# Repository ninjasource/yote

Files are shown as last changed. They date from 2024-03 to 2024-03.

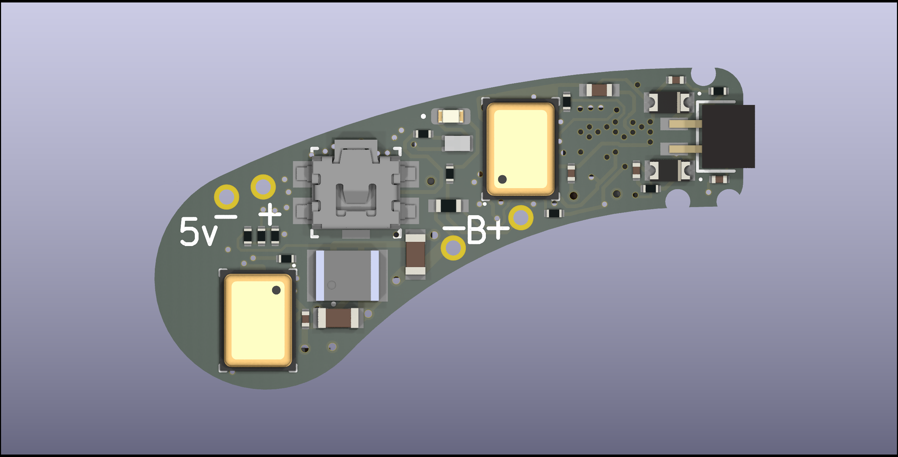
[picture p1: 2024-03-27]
kicad/yote/manufacture/yote-back.png

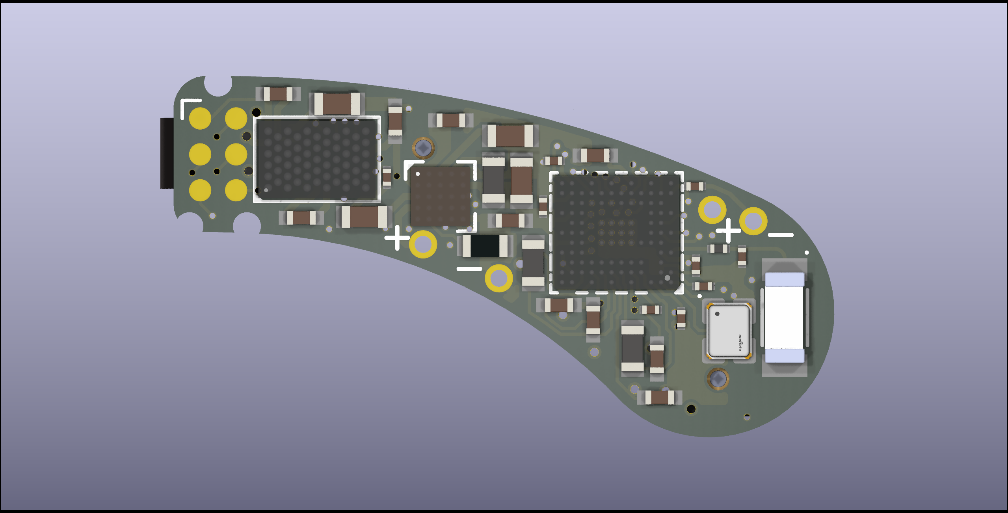
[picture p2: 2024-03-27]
kicad/yote/manufacture/yote-front.png

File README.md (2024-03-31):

# Yote - Year of the Ear

Experiments with the nrf5340 Audio Dk, CS47L63 DSP chip and Yote experimental hearing aid. 
For Rust firmware, open the `firmware` folder instead of working from this folder

## Prerequisites

`cargo install probe-rs --features="cli"`

If probe-rs does not work then a known working version can be found here:
https://github.com/probe-rs/probe-rs.git#ff2370fb

## To run

NOTE on naming:
All the examples prefixed with "yote" are for the custom built hearing aid device. Everything else is for the nRF5340 Audio-dk

IMPORTANT: be sure to set the appropriate runner in .cargo/config.toml

```
cargo run --bin blinky --release
```

## Troubleshooting

You may get an "Arm specific error at runtime and the most likely cause is that you ran probe-run with the `--erase-all` flag set.
Check the notes in `.cargo/config.toml`

Here are some commands you may find useful when working with the nrf5340 audio dk. 
You will need to install the nrfjprog command line tools from Nordic beforehand.

```
nrfjprog -i
nrfjprog --eraseall --snr 1050175639 (locks up)
nrfjprog --recover --coprocessor CP_APPLICATION --snr 1050175639
nrfjprog --recover --snr 1050175639 (same as application above)
nrfjprog --recover --coprocessor CP_NETWORK --snr 1050175639 (locks up)
```

Here is some code that you can use to flash the device without probe-run:

```
#! /usr/bin/env bash

cargo objcopy --release -- -O ihex test.hex
nrfjprog -f NRF53 --erasepage 0x00000000-0x00100000
nrfjprog -f NRF53 --program test.hex --debugreset
rm test.hex
```

## How it works

This demo uses the mcu to generate a tone and plays it into the cs47l63 dsp chip. 
Before it can do that it has to configure the dsp chip correctly by writing to various registers over spi.
There are multiple tasks running simultaneously so we need a mechanism to share the spi bus between them.

The demo runs three main tasks simultaneously: 
1. Handle interrupts from the DSP chip which indicates that long running tasks on the DSP have been completed
2. Handle button presses to control playback and volume
3. Generate a waveform in real time and push the data to the DSP chip over the I2S sound bus

## Project structure

The `cs47l63` cargo library is responsible for booting up the cs47l63 chip correctly and providing a bunch of register address and constants to be used by the application.
The `hw_dsp` (hardware digital signal processing) constrains a collection of helper functions that make calls to the `cs47l63` driver to configure it.
The `main.rs` application should use `dsp` module to exclusively communicate with the `cs47l63` even though, in theory, it could communicate directly with it through the `shared_bus` module. Right now there is some code duplication because of some power saving experiments where we need to drop the spi bus after every use. The duplicated code should be consolidated as soon as an acceptable abstraction has been designed.

## Chapro compilation

CC=arm-none-eabi-gcc
AR=arm-none-eabi-ar
CFLAGS = -W -Wall -Os -mthumb -ffunction-sections -fdata-sections -mcpu=cortex-m33 -DBR_ARMEL_CORTEXM_GCC -I$(INCDIR) -Wno-unused-local-typedef -fPIC -mfpu=fpv5-sp-d16 -mfloat-abi=hard

## Notes on Power Consumption

Here are some of the things that seem to affect power consumption:

Logging: No effect unless a debugger is attached - then huge effect
Core clock 64Mhz -> 128Mhz and Flash Cache enabled - 200uA consumption
Setting all peripheral pins to Input Low on startup - no effect, they seem to already default to their lowest power setting anyway

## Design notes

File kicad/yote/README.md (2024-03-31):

# Kicad project for schematic and PCB

Requires Kicad 8.0
Step files for the 3D rendering of the board will be checked in soon but at the moment they are not in the project path and therefore not rendered correctly. 
This messes up the PCB Design Rule checker too. Kicad projects are a little tricky to setup to work on multiple machines because of all the internal and external library files involved. 

If you do not have the correct version of Kicad installed then you can use the exported PDF schematic below:

Please see output/yote.pdf for now

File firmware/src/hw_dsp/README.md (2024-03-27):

# Hardware DSP

This module interfaces with the CS47L63 driver. The module consists of a collection of register values known to work with the nRF5340 Audio DK and Yote. It also exposes a shared bus to let different async tasks share the same SPI bus.
This shared bus design is no good for low power since it currently does not disable the SPI bus after use. Therefore there are duplicate `_spi` prefixed functions that do the same thing but without a mutex. This should be fixed soon.

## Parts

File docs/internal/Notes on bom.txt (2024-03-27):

100n
power decoupling caps: GRM033R61A104ME15D
Why? 10V Thats what was used in this video: https://www.youtube.com/watch?v=kUruN6WBgSw (see time 20:04)
Available cheaply from JLCPCB

1u
power decoupling caps: GRM033R60J105KEA2D
Why? 6.3V Available as 0201 (can't find 0402)
Available cheaply from JLCPCB

# command for generating bom:
/usr/bin/python3 "/usr/share/kicad/plugins/bom_csv_grouped_extra.py" "%I" "%O.csv" "PACKAGE" "MANUFACTURER" "Mfg Part #" "Notes"

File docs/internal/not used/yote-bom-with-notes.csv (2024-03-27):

Ref | Qnty | Value | Cmp name | Footprint | Description | Vendor | Mrf Part # | Jlcpcb part # | Notes
C1, C2, C3, C4, C5, C15, C19, C20, C21, C24, C26, C27 | 12 | 100n | C_Small | nrf5340:C_0201_0603Metric_Square | Capacitor, X5R, ±10% | Murata Electronics | GRM033R61A104ME15D | C408130
C7, C8, C9, C13, C14, C16, C22, C23, C25 | 9 | 1u | C_Small | nrf5340:C_0402_1005Metric_Square | Capacitor, X5R, ±10%, 6.3V | Murata Electronics | GRM155R60J105KE19D | C76929
C10 | 1 | 2n2 | C_Small | nrf5340:C_0201_0603Metric_Square | Capacitor, X7R, ±10%, 10V | Murata Electronics | GRM033R71A222KA01D | C161479
C11 | 2 | 0p7 | C_Small | nrf5340:C_0201_0603Metric_Square | Capacitor, Ceramic, NP0, ±0.1pF, 25V | Murata Electronics | GJM0335C1ER70BB01D | C161293 | Can’t find on jlcpcb, use global sourcing
C28, C30 | 1 | 2u2 | C_Small | nrf5340:C_0402_1005Metric_Square | Capacitor, Ceramic, X5R, ±10%, 10V | Murata Electronics | GRM155R61A225KE95D | C76993
C29, C31, C32, C33, C35 | 5 | 10u | C_Small | nrf5340:C_0603_1608Metric_Square | Capacitor, Ceramic, X5R, ±20%, 10V | Murata Electronics | GRM188R61A106KE69D | C77044
C34 | 1 | 22u | C_Small | nrf5340:C_0603_1608Metric_Square | Capacitor, X5R, ±20%, 6.3V | Murata Electronics | GRM188R61A226ME15D | C84419
D1, D2, D4 | 3 | PESD5V0V1BDSF | PESD5V0V1BDSF | nrf5340:D_0603_1608Metric_Square | Very low capacitance bidirectional ESD protection diode | Nexperia | PESD5V0V1BDSF,315 | C513113
D3 | 1 | RED_LED | LED | LED_SMD:LED_0402_1005Metric | Light emitting diode | Foshan NationStar Optoelectronics | NCD0402R1 | C130719
E1 | 1 | 2450AT18B100E | 2450AT18B100E | nrf5340:2450AT18B100E | 2.45 GHz chip antenna | Johanson Technology | 2450AT18B100E | C2917717
J2 | 1 | BC075-02-A-L-A | BC075-02-A-L-A | nrf5340:BC075-02-A-L-A | 2POS 1.0MM PITCH SOCKET, SIL, SM | GCT | BC075-02-A-L-A |  | Part no longer manufactured (by jlcpcb) but available on digikey
L1, L4 | 2 | 10u | L_Small | nrf5340:L_0603_1608Metric_MLZ1608M100WTD25 | Inductor, 250mA, ±20%, 1.05ohm. -55°C ~ 125°C | TDK | MLZ1608M100WTD25 | C2047264
L2, L3 | 2 | 2n2 | L_Small | nrf5340:L_0201_0603Metric_Square | Inductor, 600mA, ±0.1ｎH, 120mOhm | Murata Electronics | LQP03HQ2N2B02D | C1329438
L5 | 1 | 4n7 | L_Small | nrf5340:L_0201_0603Metric_Square | Inductor, 350mA, ±3% | Murata Electronics | LQP03TN4N7H02D | C86126 | As per dk bom
L6 | 1 | 2u2 | L_Small | nrf5340:L_0603_1608Metric_MLZ1608M100WTD25 | 750mA 2.2uH ±20% 390mΩ 0603 Inductors | TDK | MLP1608H2R2BT0S1 | C129931 | This is a 750mA rated part but on the dk it is a 2.5A rated part
R1, R2 | 2 | 100 | R_Small | nrf5340:R_0201_0603Metric_Square | Resistor, ±1%, 0.05W | YAGEO | RC0201FR-07100RL | C77623 | For stability of data line of mics
R3, R4 | 2 | 22 | R_Small | nrf5340:R_0201_0603Metric_Square | Resistor, ±1%, 0.05W | YAGEO | RC0201FR-0722RL | C155743 | For stability on headphone line
R5 | 1 | 100k | R_Small | nrf5340:R_0201_0603Metric_Square | Resistor, small symbol | YAGEO | RC0201FR-07100KL | C106224
R6 | 1 | 33k | R_Small | nrf5340:R_0603_1608Metric_Square | Resistor, small symbol | UNI-ROYAL | 0603WAF3302T5E | C4216 | Large so that it can be de-soldered (controls charging current) Basic part
R7, R8, R9 | 3 | 1M | R_Small | nrf5340:R_0201_0603Metric_Square | Resistor, small symbol | YAGEO | RC0201FR-071ML | C295786 | Voltage divider for batt measurement
R10 | 1 | 33 | R_Small | nrf5340:R_0402_1005Metric_Square | Resistor, small symbol | YAGEO | RC0402FR-0733RL | C138002 | For the red led
S1 | 1 | Volume Up | PTS840_GM_SMTR_LFS | nrf5340:SW_PTS840GMSMTRLFS | Push button switch | C&K | PTS840GMSMTRLFS | C221909
TH1 | 1 | Thermistor_NTC | Thermistor_NTC | nrf5340:R_0402_1005Metric_Square | 10kΩ 0.1mA ±1% 3380K ±1% 0402 NTC Thermistor | Murata Electronics | NCU15XH103F6SRC | C333993 | If no thermister then 10k resistor is fine
U1 | 1 | NRF5340-CLAA-R | NRF5340-CLAA-R | nrf5340:NRF5340-CLAA-R |  | Nordic Semiconductor | NRF5340-CLAA-R | C3606597
U2, U3 | 2 | IM69D130_PDM | IM69D130_PDM | nrf5340:MIC_IM69D130V01XTSA1_PadFix |  | Infineon Technologies | IM69D130V01XTSA1 |  | Not the same as the one on the Audio Dk. Says its no longer manufactured on jlcpcb. Available on digikey
U4 | 1 | CS47L63-CWZR | CS47L63-CWZR | nrf5340:CS47L63-CWZR |  | Cirrus Logic | CS47L63-CWZR | C3588069
U5 | 1 | NPM1100-CAAA-R7 | NPM1100-CAAA-R7 | nrf5340:NPM1100-CAAA-R7 |  | Nordic Semiconductor | nPM1100-CAAA-R7 | C3682614 | The NPM1100-CAAA-E-R7 variant on digikey is $2 (vs $10 for the the R7)
U6 | 1 | XCL210C12 | XCL210C12 | nrf5340:XCL210C12 |  | Torex Semiconductor | XCL210C121GR-G |  | Only available on Mouser
Y1 | 1 | 32Mhz 8pF | Crystal_GND24_Small | nrf5340:MP06003_Crystal | Four pin crystal, GND on pins 2 and 4, small symbol | Kyocera | CX2016DB32000D0WZRC1 | C1985237 | As per dk bom

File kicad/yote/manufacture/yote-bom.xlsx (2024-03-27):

 |  |  | YOTE – Bill of Materials
Item # | *Designator | *Qty | Manufacturer | *Mfg Part # | Description / Value | *Package/Footprint | Type | Your Instructions / Notes
1 | C1, C2, C3, C4, C5, C15, C19, C20, C21, C24, C26, C27 | 12 | Murata Electronics | GRM033R61A104KE15D | 100n | 0201 |  | Capacitor, X5R, ±10%
2 | C7, C8, C9, C13, C14, C16, C22, C23, C25 | 9 | Murata Electronics | GRM155R60J105KE19D | 1u | 0402 |  | Capacitor, X5R, ±10%, 6.3V
3 | C10 | 1 | Murata Electronics | GRM033R71A222KA01D | 2n2 | 0201 |  | Capacitor, X7R, ±10%, 10V
4 | C11 | 1 | Murata Electronics | GRM0335C1HR70WA01D | 0p7 | 0201 |  | Capacitor, NP0, ±0.1pF
5 | C28, C30 | 2 | Murata Electronics | GRM155R61A225KE95D | 2u2 | 0402 |  | Capacitor, X5R, ±20%
6 | C29, C31, C32, C33, C35 | 5 | Murata Electronics | GRM188R61A106KE69D | 10u | 0603 |  | Capacitor, Ceramic, X5R, ±20%, 10V
7 | C34 | 1 | Murata Electronics | GRM188R61A226ME15D | 22u | 0603 |  | Capacitor, X5R, ±20%, 6.3V
8 | D1, D2 | 2 | Nexperia | PESD5V0V1BDSF,315 | PESD5V0V1BDSF | 0603 |  | Very low capacitance bidirectional ESD protection diode
9 | D3 | 1 | Everlight Elec | 16-213SYGC/S530-E3/TR8 | GREEN_LED | 0402 |  | Green LED 2V forward voltage 25mA max
10 | E1 | 1 | Johanson Technology | 2450AT18B100E | ANT | SMD |  | 2.45 GHz chip antenna
11 | H3 | 1 |  |  | 5V | DNS |  | Footprint only – Do not place
12 | H4 | 1 |  |  | GND | DNS |  | Footprint only – Do not place
13 | H5 | 1 |  |  | BATT+ | DNS |  | Footprint only – Do not place
14 | H6 | 1 |  |  | BATT- | DNS |  | Footprint only – Do not place
15 | J1 | 1 |  |  | TC2030-NL | DNS |  | Footprint only – Do not place
16 | J2 | 1 | GCT | BC075-02-A-L-A | 2POS_FEMALE_1mm | SMD |  | 2POS 1.0MM PITCH SOCKET, SIL, SM
17 | L1, L4 | 2 | TDK | MLZ1608M100WTD25 | 10u | 0603 |  | Inductor, 250mA, ±20%, 1.05ohm. -55°C ~ 125°C
18 | L2 | 1 | Murata Electronics | LQP03HQ2N2B02 | 2n2 | 0201 |  | Inductor, 600mA, ±0.1ｎH, 120mOhm
19 | L6 | 1 | TDK | MLP1608H2R2BT0S1 | 2u2 | 0603 |  | 750mA 2.2uH ±20% 390mΩ 0603 Inductors
20 | Q1 | 1 | Tech Public | TP5001P3 | NPN_TRANSISTOR | SMD |  | NPN Transistor of with Hfe of around 100 for LED
21 | R1, R2 | 2 | YAGEO | RC0201FR-07100RL | 100 | 0201 |  | Resistor
22 | R3, R4 | 2 | YAGEO | RC0201FR-0722RL | 22 | 0201 |  | Resistor
23 | R5 | 1 | YAGEO | RC0201FR-07100KL | 100k | 0201 |  | Resistor
24 | R6 | 1 | UNI-ROYAL | 0603WAF3302T5E | 33k | 0603 |  | Resistor
25 | R7, R8, R9 | 3 | YAGEO | RC0201FR-071ML | 1M | 0201 |  | Resistor
26 | R10 | 1 | YAGEO | RC0201FR-071KL | 1k | 0201 |  | Resistor
27 | R11 | 1 | YAGEO | RC0201FR-07330RL | 330 | 0201 |  | Resistor
28 | S1 | 1 | C&K | PTS840GMSMTRLFS | PUSH_BTN | SMD |  | Push button sideways switch
29 | TH1 | 1 | Murata Electronics | NCU15XH103F6SRC | Thermistor_NTC | 0402 |  | 10k 0.1mA ±1% 3380K ±1% 0402 NTC Thermistor
30 | U1 | 1 | Nordic Semiconductor | NRF5340-CLAA | NRF5340-CLAA-R | SMD |  | nRF5340 microcontroller
31 | U2, U3 | 2 | Infineon Technologies | IM69D130V01XTSA1 | IM69D130_PDM | SMD |  | IM69D130 PDM microphone
32 | U4 | 1 | Cirrus Logic | CS47L63-CWZR | CS47L63-CWZR | SMD |  | CS47L63 digital signal processing IC
33 | U5 | 1 | Nordic Semiconductor | NPM1100-CAAA | NPM1100-CAAA-R7 | SMD |  | nPM1100 battery charger
34 | U6 | 1 | Torex Semiconductor | XCL210C121GR-G | XCL210C12 | SMD |  | 1_2V dcdc converter
35 | Y1 | 1 | Kyocera | CX2016DB32000D0WZRC1 | 32Mhz 8pF | CX2016 |  | Four pin crystal, GND on pins 2 and 4, small symbol, 32mhs 8pF

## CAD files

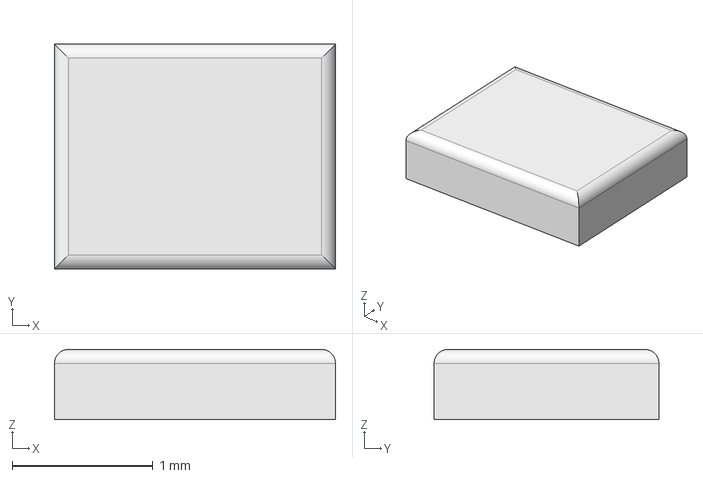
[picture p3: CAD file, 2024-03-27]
freecad/crystal/R2016-32Mhz-8pF-Crystal-Fillet.step
2.00 x 1.60 x 0.5 mm

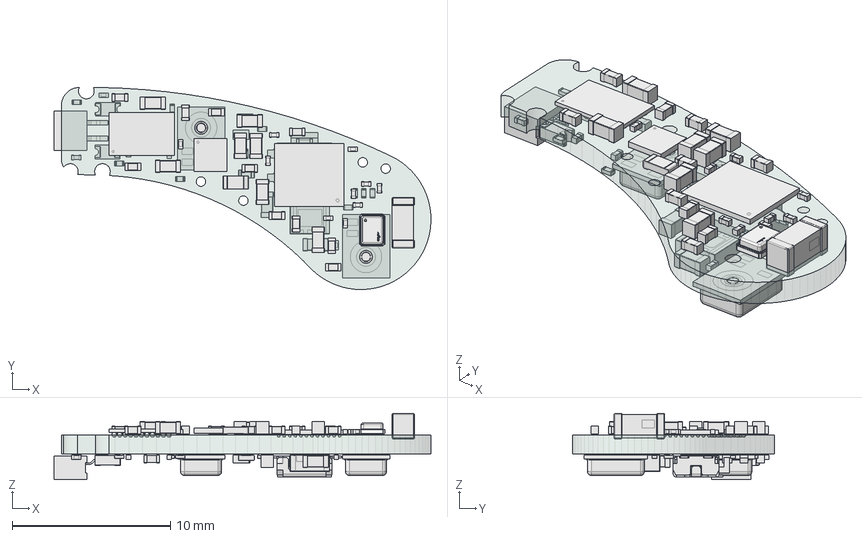
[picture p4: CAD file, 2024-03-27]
freecad/full/board.FCStd
23.8 x 12.8 x 4.17 mm
C_0402_1005Metric
L_0603_1608Metric
C_0402_1005Metric002
logo
dot
pins
C_0603_1608Metric
C_0201_0603Metric
C_0603_1608Metric002
L_0201_0603Metric
C_0201_0603Metric002
C_0402_1005Metric004
C_0201_0603Metric004
NPM1100-CAAA-R7
2450AT18B100E
C_0201_0603Metric006
C_0402_1005Metric006
C_0201_0603Metric008
C_0402_1005Metric008
C_0402_1005Metric010
C_0402_1005Metric012
C_0201_0603Metric010
C_0603_1608Metric004
C_0201_0603Metric012
C_0603_1608Metric006
R_0603_1608Metric
C_0402_1005Metric014
L_0603_1608Metric002
C_0402_1005Metric016
C_0201_0603Metric014
C_0402_1005Metric018
C_0201_0603Metric016
L_0603_1608Metric004
R_0201_0603Metric
C_0201_0603Metric018
C_0402_1005Metric020
R_0201_0603Metric002
R_0201_0603Metric004
C_0201_0603Metric020
D_0603
R_0201_0603Metric006
Y97M01840FP_G
R_0201_0603Metric008
C_0603_1608Metric008
C_0201_0603Metric022
IM69D130V01XTSA1
IM69D130V01XTSA003
XCL220B153FR-G
C_0201_0603Metric024
R_0201_0603Metric010
BC075-02-A-L-A
LED_0402_1005Metric
C_0201_0603Metric026
R_0201_0603Metric012
D_0604
R_0201_0603Metric014
R_0201_0603Metric016
R_0201_0603Metric018
C_0603_1608Metric010
R_0402_1005Metric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

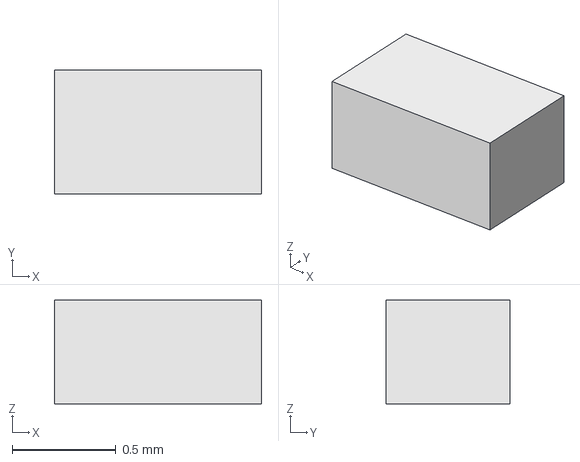
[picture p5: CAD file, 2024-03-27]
freecad/npn transistor/npn.FCStd
1.00 x 0.6 x 0.5 mm

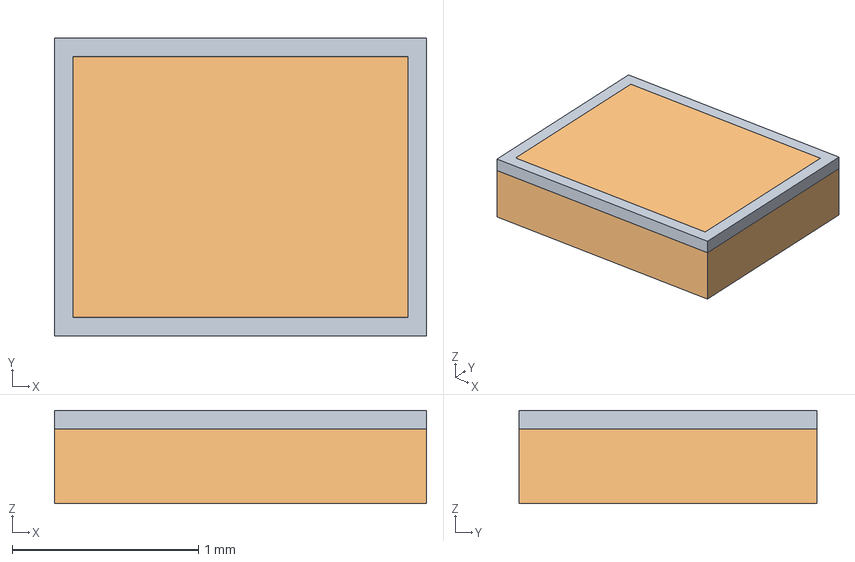
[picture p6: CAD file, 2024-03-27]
freecad/crystal/R2016-32Mhz-8pF-Crystal.FCStd
2.00 x 1.60 x 0.5 mm

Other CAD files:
freecad/npn transistor/TP5001P3.step

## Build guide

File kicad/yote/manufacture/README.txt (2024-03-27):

All vias (0.5/0.3mm and 0.3/0.15mm) to be filled and capped (because 0.3/0.15mm via-in-pad used for 0.4mm pitch bga components).
Panelization: PCWWay to please panlize board to 2 x 3 and increase the panel size accordingly.
Silkscreen: It is acceptable to not show Silkscreen on non-printable areas.
Please confirm rotation of components in a visual way with me to make sure it is correct (silkscreen should provide markers and CGI render can be used too).
Min track / spacing: 3mil
Min hole size: 0.15mm

Impedance control:

The track that connects the MCU to the antenna needs to be impedance matched to 50 ohms. Here are the calculations:

Used this calculator for surface microstrip for antenna line:
https://www.pcbway.com/pcb_prototype/impedance_calculator.html

w      = 0.134mm (calculated track width)
t Cu   = 35um (track height - I included the plating - should I have?)
h      = 0.08mm (isolation height)
Er     = 4.29 (Dialectric constant - FR4 - Standard 4.3)
Z0     = 50.0 ohm (Impedance)
Layer  = L1 (Front - yote-F_Cu.gbr)
Type   = Single ended
Pos    = x 19.45 y 6.85 (the short transmission line that L2 sits on going from the nrf5340 mcu to the antenna)
Tollerance = 10%

Used this stackup tool:
https://www.pcbway.com/multi-layer-laminated-structure.html?tdsourcetag=s_pcqq_aiomsg

Board Stackup:

Use PCBWay defaults for 8 layer board 1mm thickness
Number of Layers:   8
Board Thickness:    1 mm
Copper thickness:   1 oz

Stackup:

L1	 	Copper 18 um--plating to 35um
 	 	 
 	 	PP 0.08 mm(1080) dielectric constant 4.29 ± (The DK value is not absolute and will vary depending on the base material's models and thickness.)
 	 	 
L2	 	 
 	 	Core 0.2mm with 1/1 oz Cu
L3	 	 
 	 	 
 	 	PP 0.08 mm(1080) dielectric constant 4.29 ± (The DK value is not absolute and will vary depending on the base material's models and thickness.)
 	 	 
L4	 	 
 	 	Core 0.2mm with 1/1 oz Cu
L5	 	 
 	 	 
 	 	PP 0.08 mm(1080) dielectric constant 4.29 ± (The DK value is not absolute and will vary depending on the base material's models and thickness.)
 	 	 
L6	 	 
 	 	Core 0.2mm with 1/1 oz Cu
L7	 	 
 	 	 
 	 	PP 0.08 mm(1080) dielectric constant 4.29 ± (The DK value is not absolute and will vary depending on the base material's models and thickness.)
 	 	 
L8	 	Copper 18 um--plating to 35um

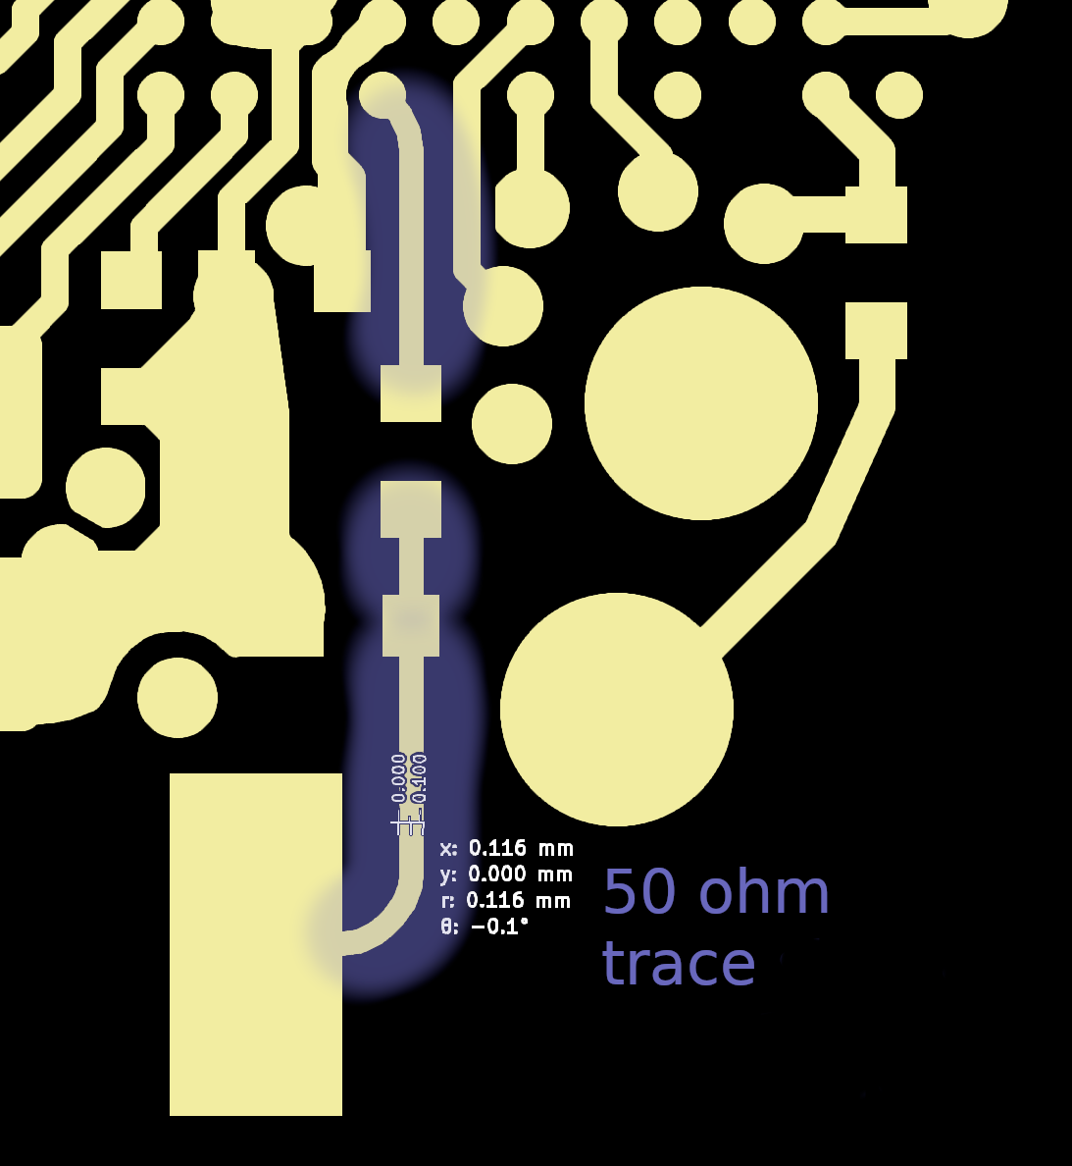
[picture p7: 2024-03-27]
kicad/yote/manufacture/gtl-impedance trace.png

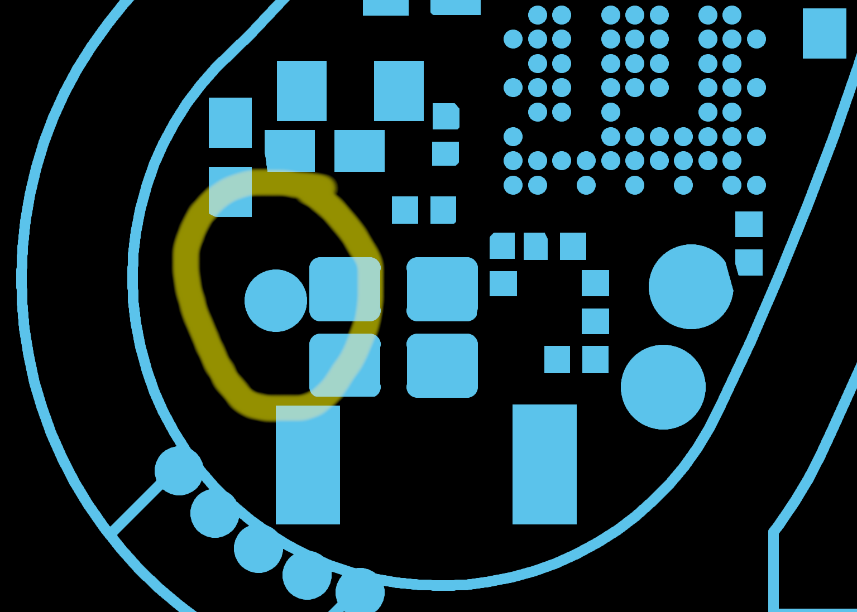
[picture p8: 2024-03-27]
kicad/yote/manufacture/gts-mic hole proximity.png

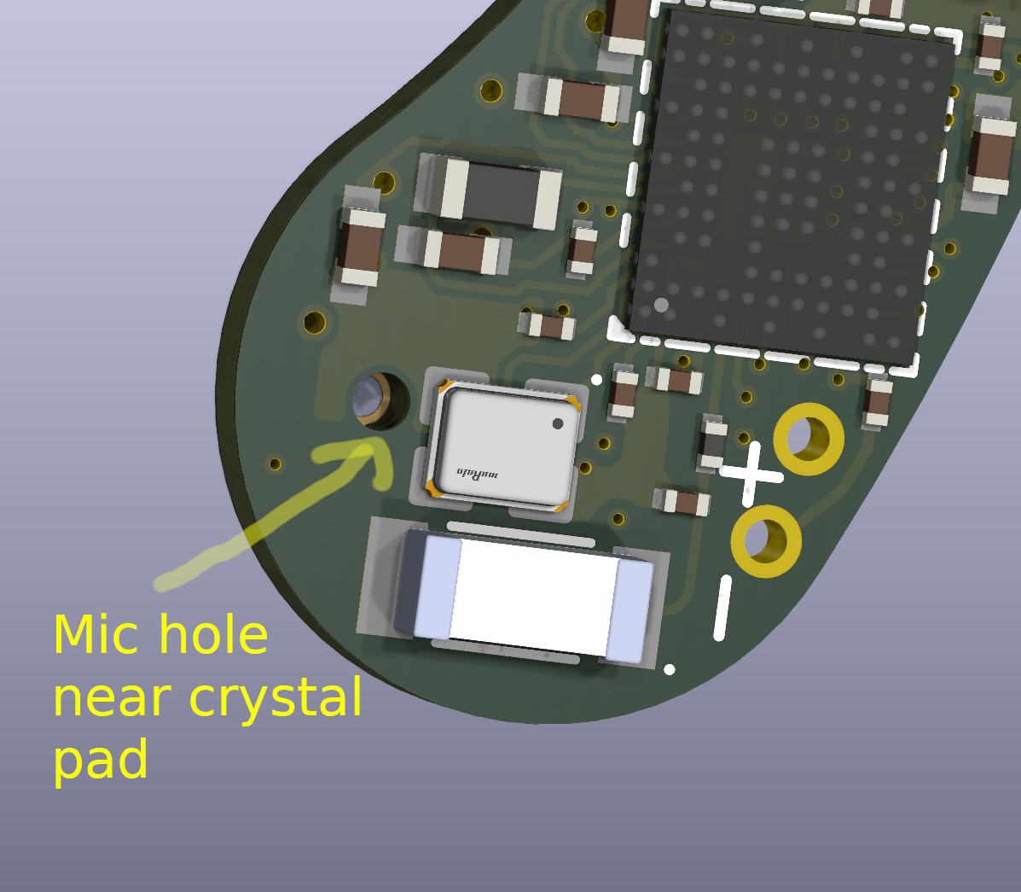
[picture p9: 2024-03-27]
kicad/yote/manufacture/gts-mic hole render.png

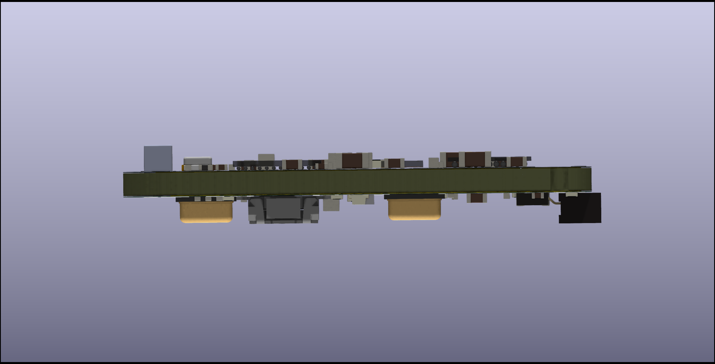
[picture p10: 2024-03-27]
kicad/yote/manufacture/yote-side.png

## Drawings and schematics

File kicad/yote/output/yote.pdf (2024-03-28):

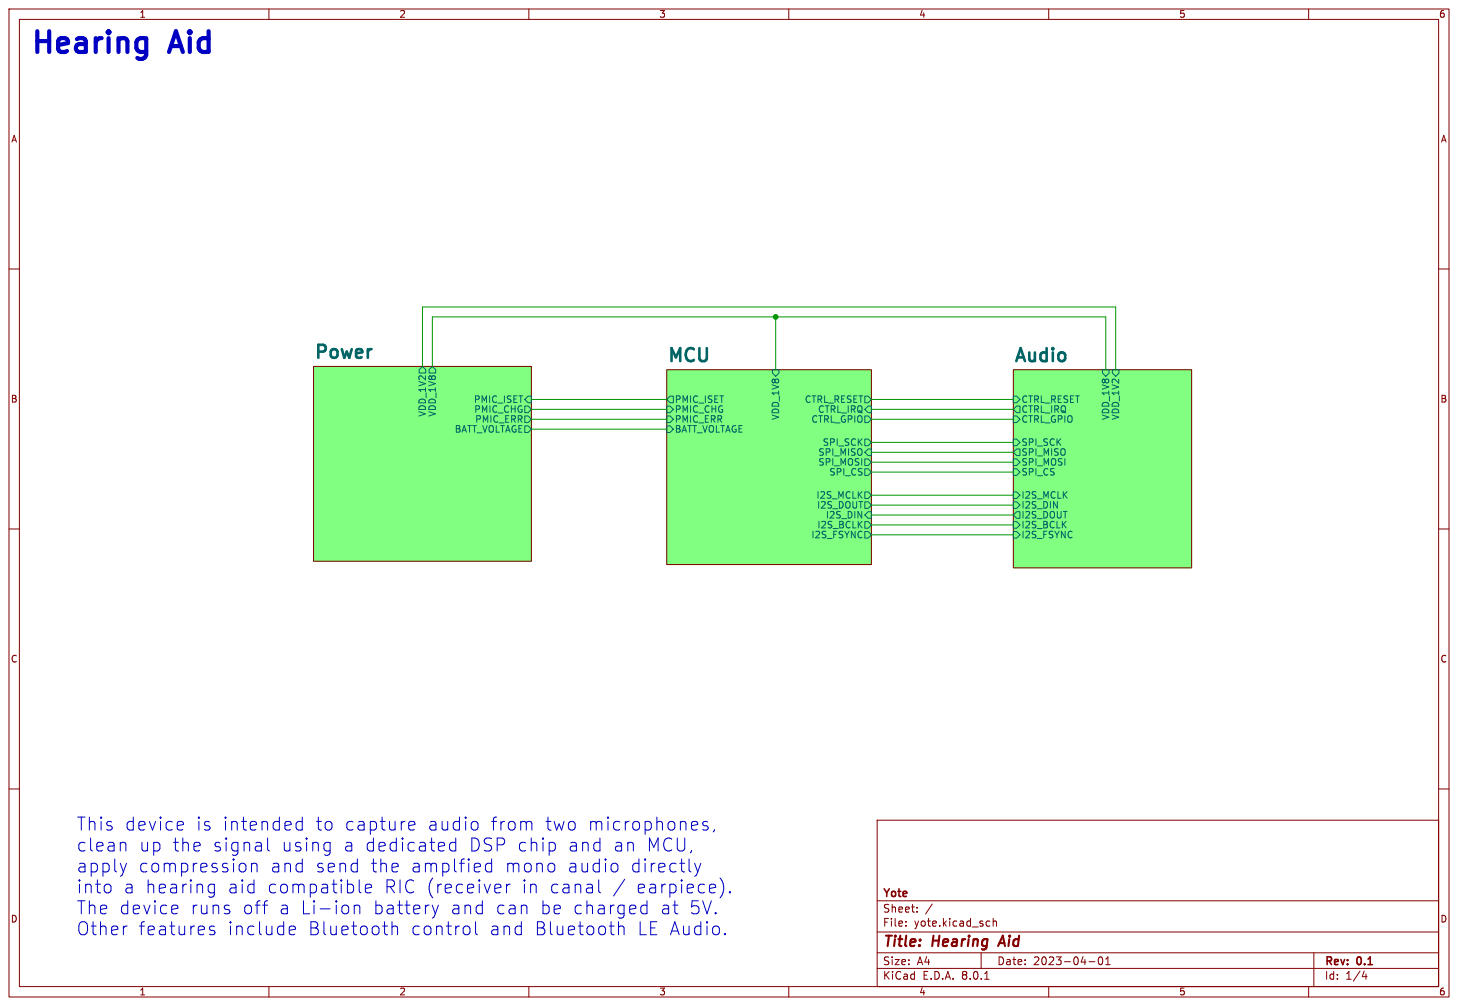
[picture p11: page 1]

File: yote.kicad_sch Sheet: / Yote

Id: 1/4 Title: Hearing Aid

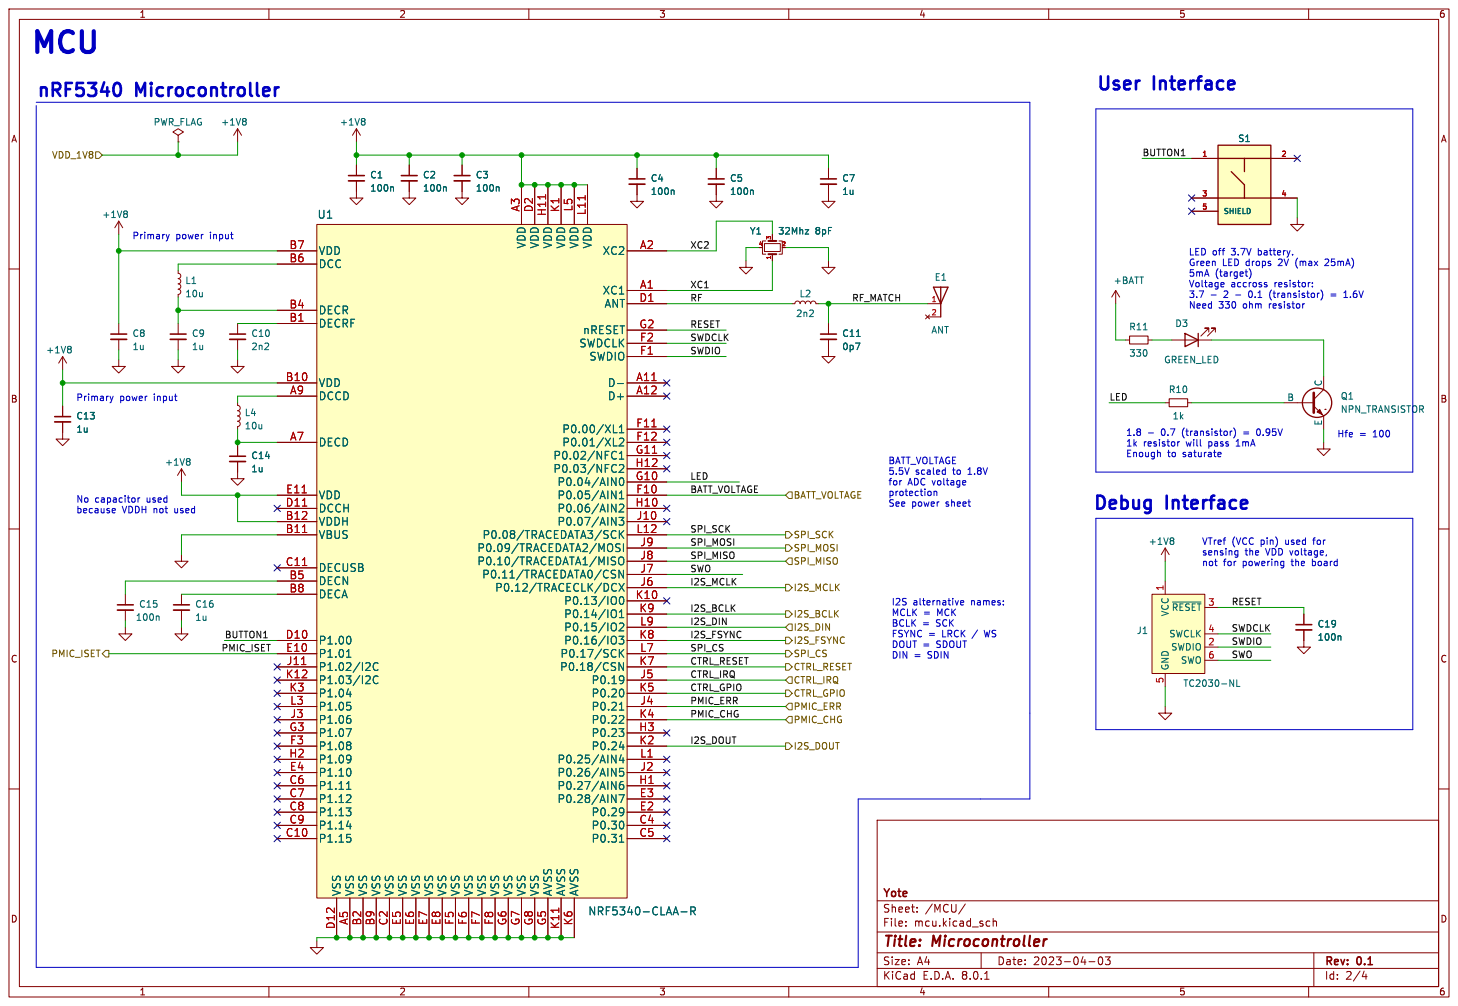
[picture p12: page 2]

because VDDH not used MCU

LED off 3.7V battery. Green LED drops 2V (max 25mA) 5mA (target)

1 SWDIO 2 ~{RESET}3 SWCLK 4 GND

Id: 2/4 Title: Microcontroller File: mcu.kicad_sch Sheet: /MCU/ Yote C16

BCLK = SCK
FSYNC = LRCK / WS DOUT = SDOUT DIN = SDIN

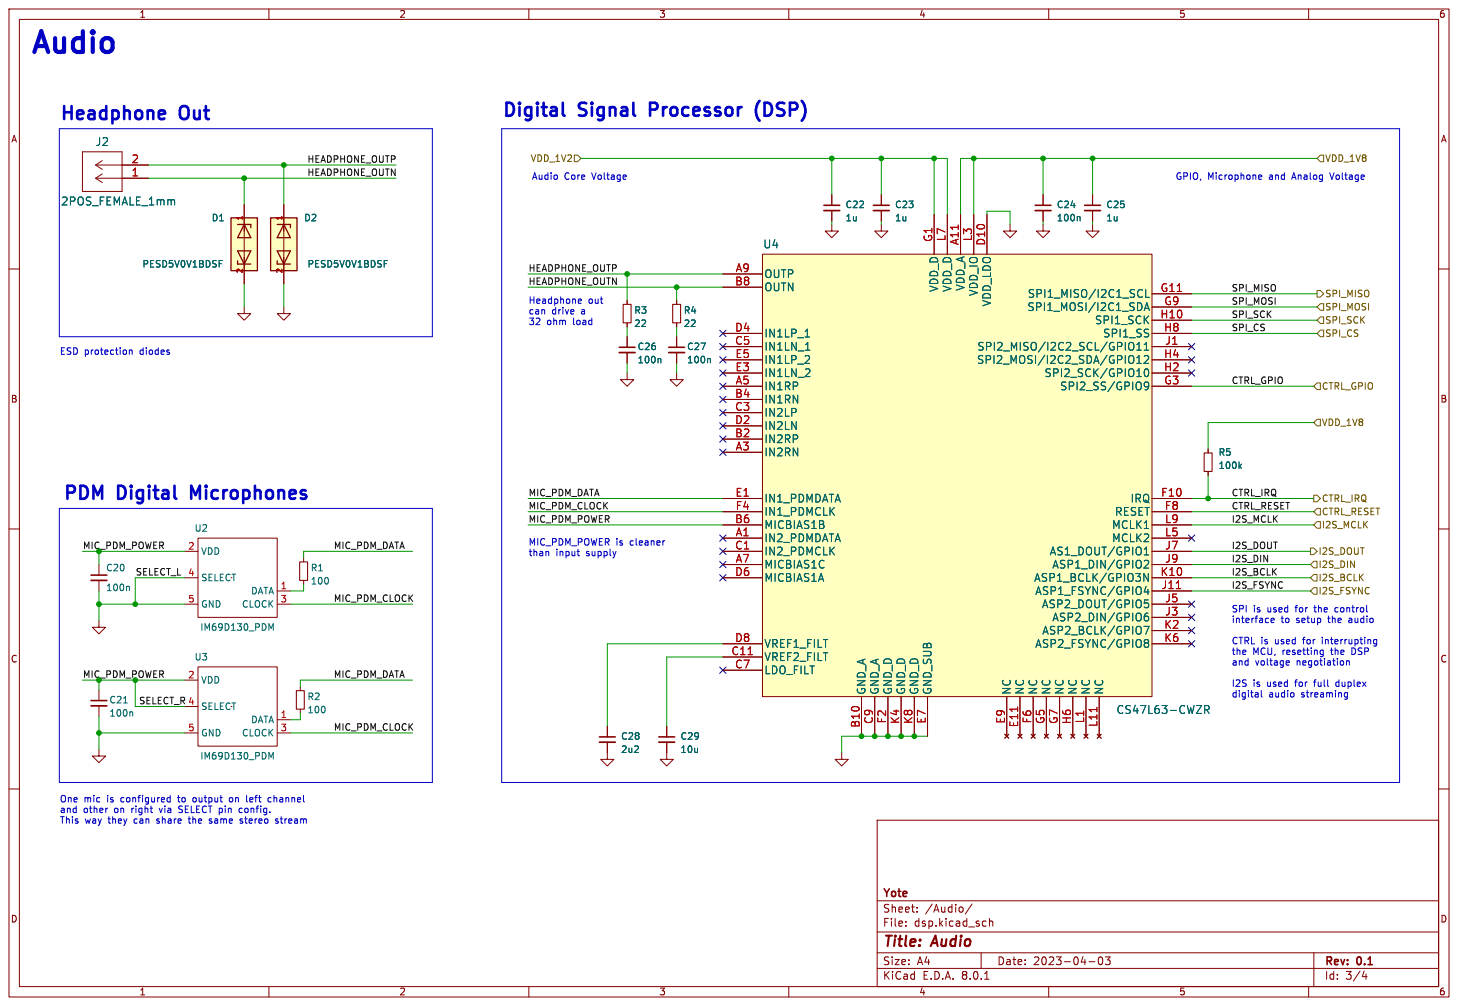
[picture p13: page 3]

1 2 D1 PESD5V0V1BDSF DATA 1 VDD 2 CLOCK 3 SELECT 4 GND 5 U2

HEADPHONE_OUTN
Headphone out can drive a

I2S is used for full duplex

File: dsp.kicad_sch Sheet: /Audio/ Yote

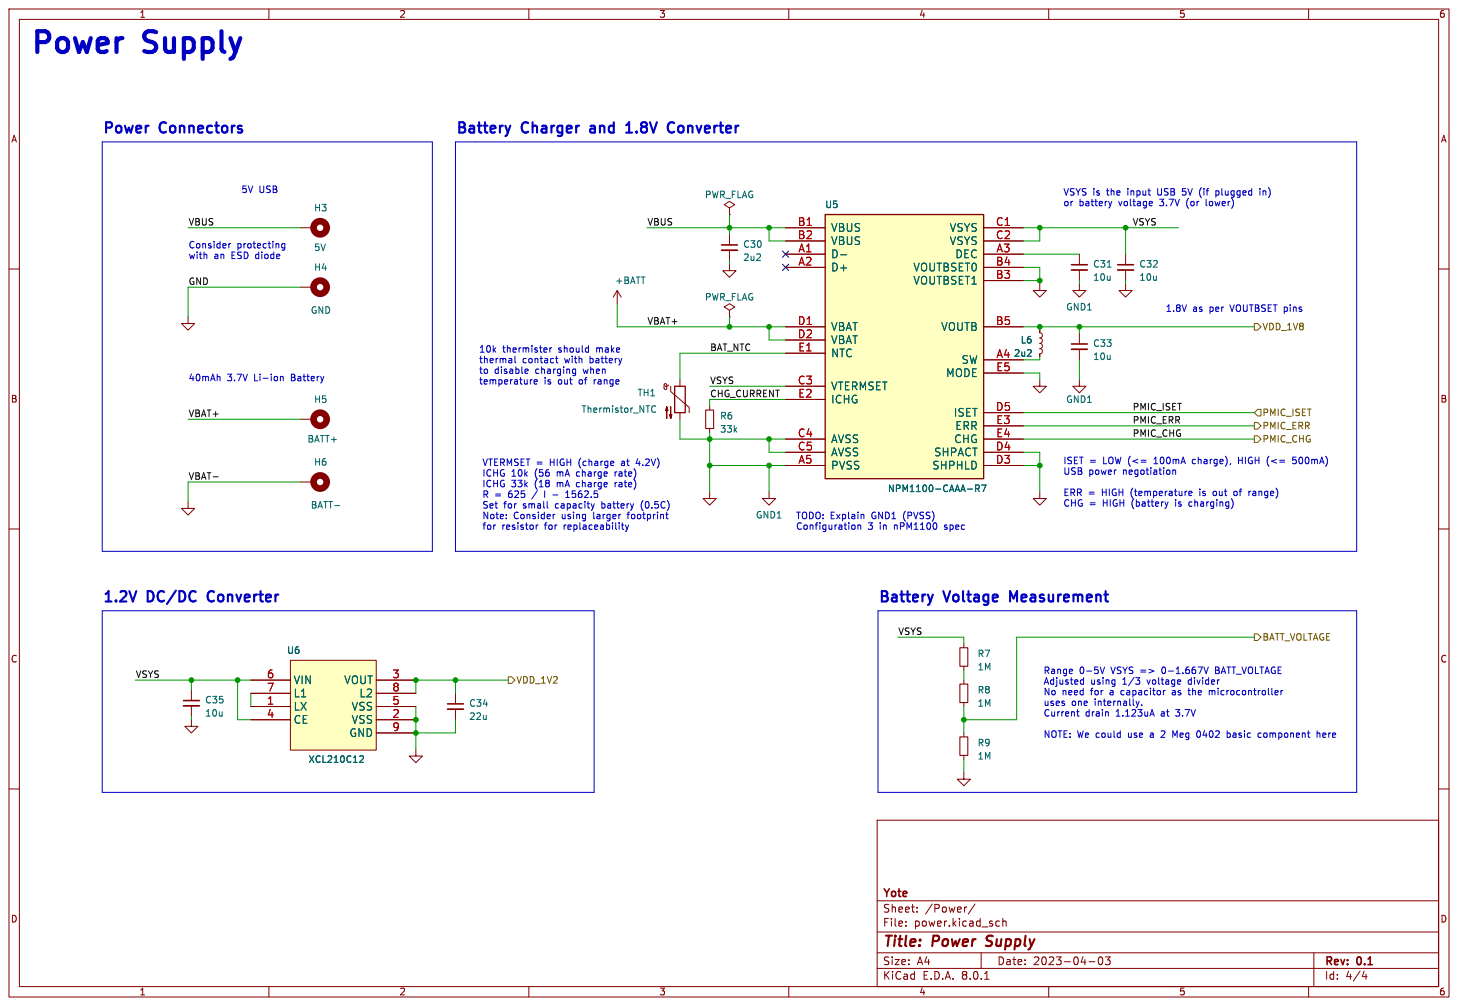
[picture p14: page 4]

ICHG 10k (56 mA charge rate)

File: power.kicad_sch Sheet: /Power/ Yote

Id: 4/4 Title: Power Supply

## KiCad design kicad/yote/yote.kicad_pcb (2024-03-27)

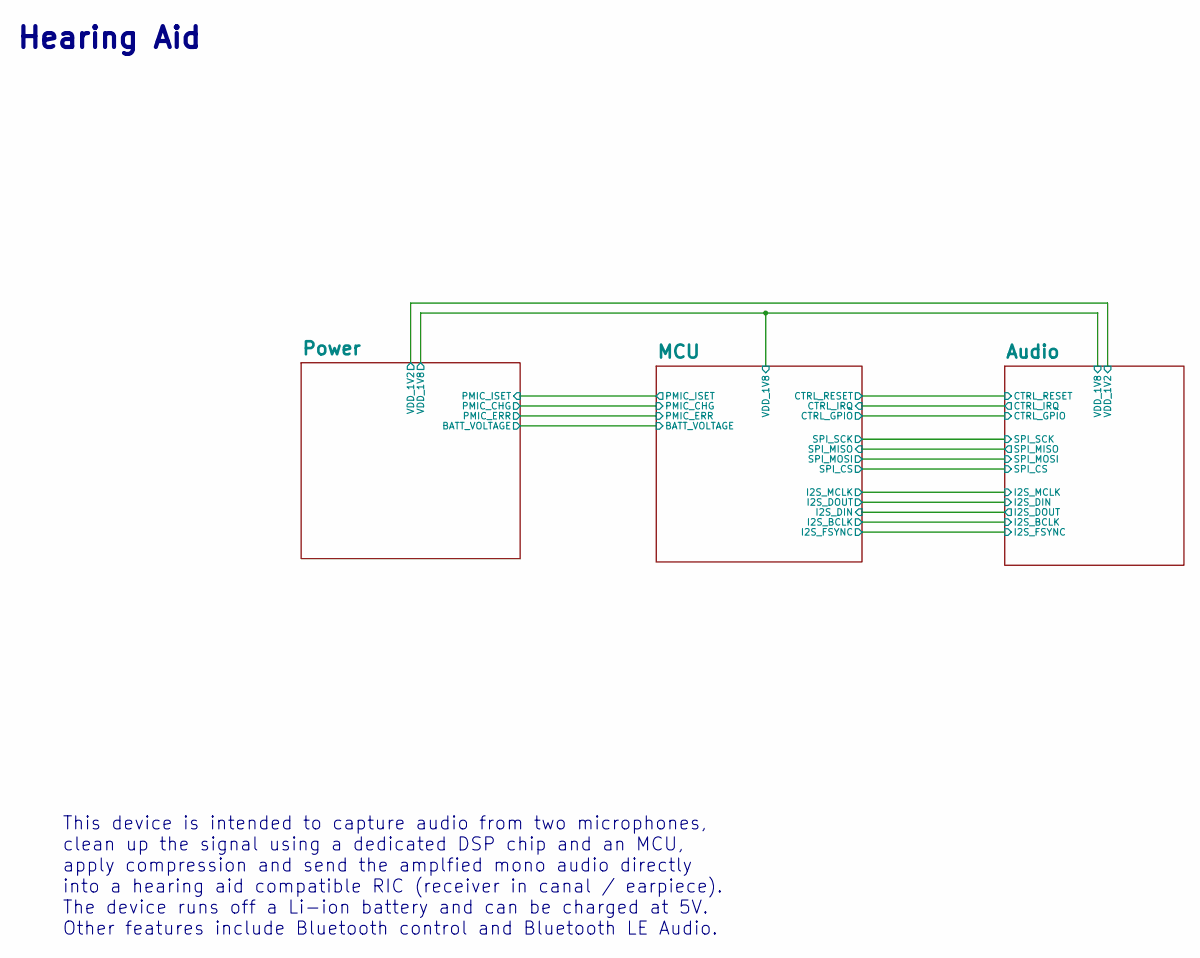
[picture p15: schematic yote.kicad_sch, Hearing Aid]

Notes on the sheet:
Hearing Aid
This device is intended to capture audio from two microphones, clean up the signal using a dedicated DSP chip and an MCU, apply compression and send the amplfied mono audio directly into a hearing aid compatible RIC (receiver in canal / earpiece). The device runs off a Li-ion battery and can be cha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

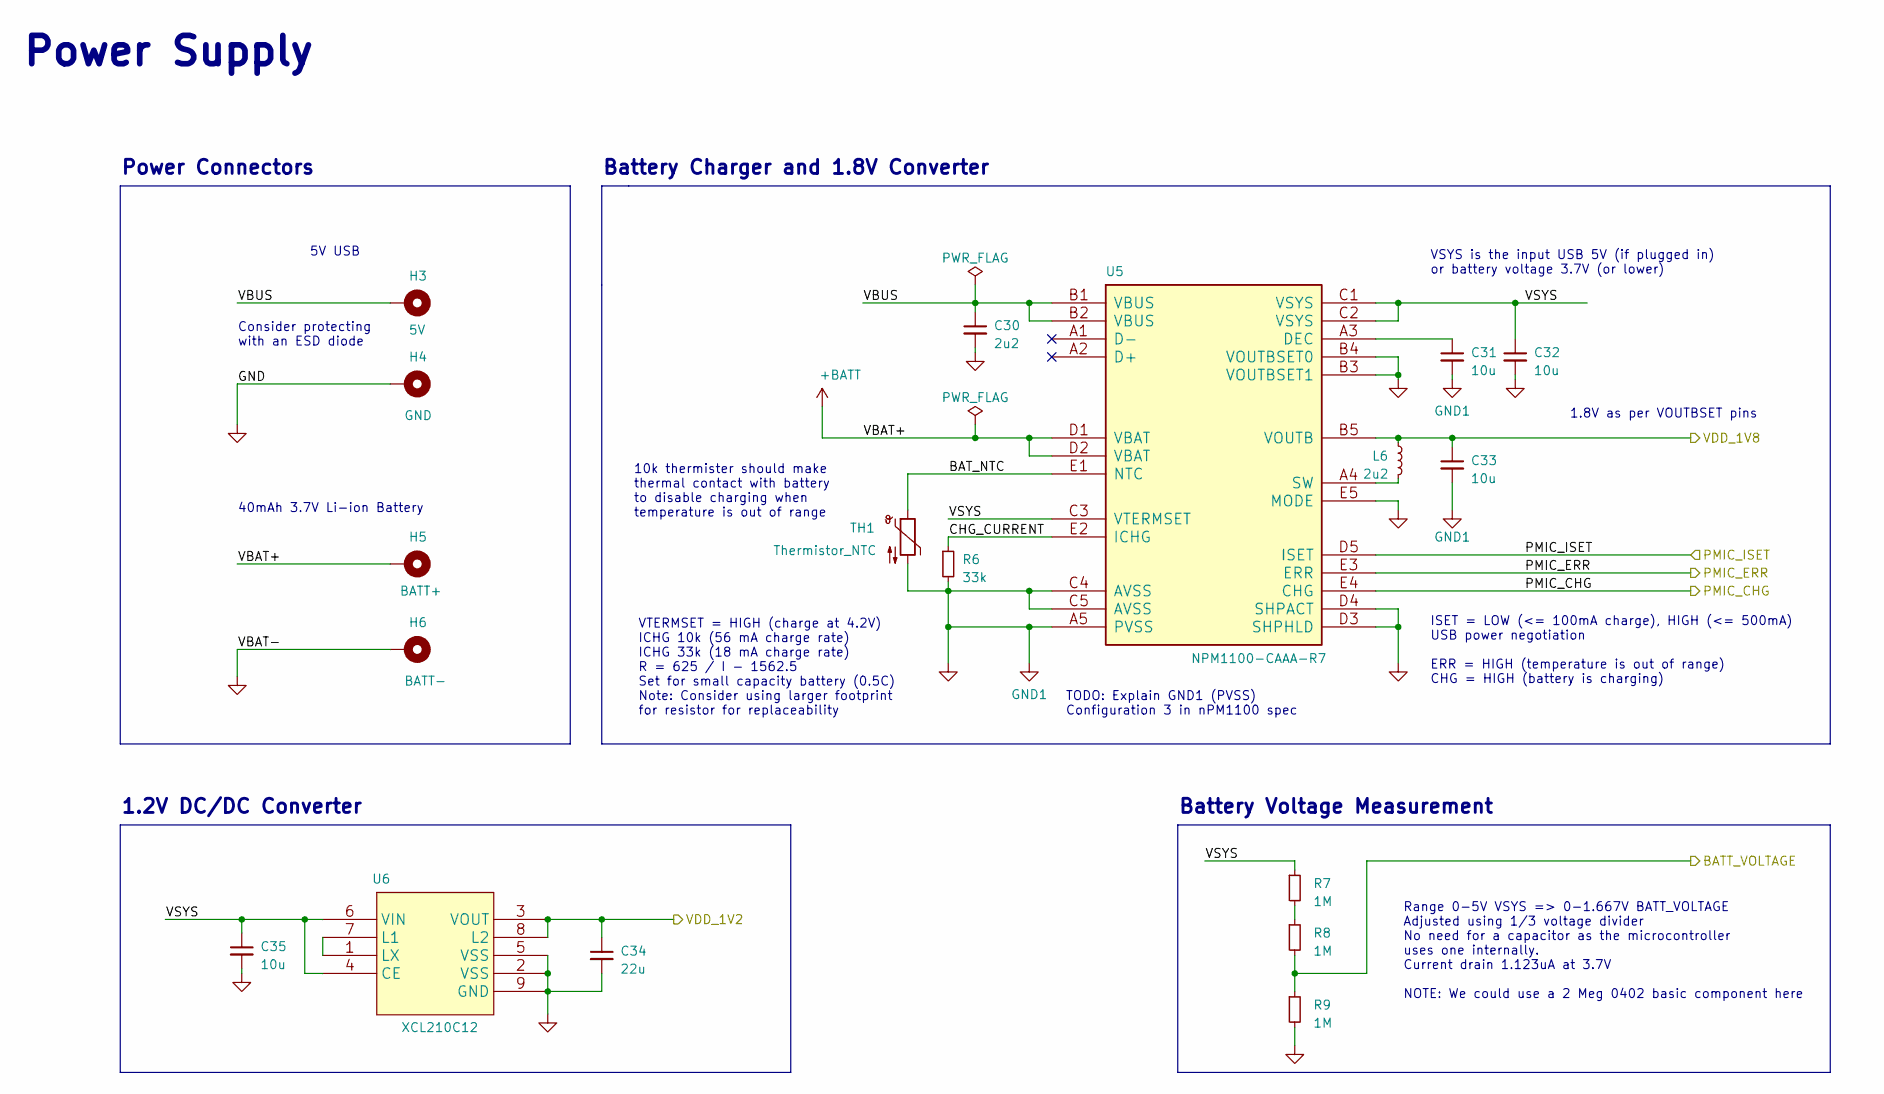
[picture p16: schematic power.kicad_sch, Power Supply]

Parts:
C30: 2u2; C_0402_1005Metric_Square; Mfg Part # GRM155R61A225KE95D
C31, C32, C33, C35: 10u; C_0603_1608Metric_Square; Mfg Part # GRM188R61A106KE69D
C34: 22u; C_0603_1608Metric_Square; Mfg Part # GRM188R61A226ME15D
H3: 5V; MountingHole_0.6mm_Pad_TopBottom
H4: GND; MountingHole_0.6mm_Pad_TopBottom
H5: BATT+; MountingHole_0.6mm_Pad_TopBottom
H6: BATT-; MountingHole_0.6mm_Pad_TopBottom
L6: 2u2; L_0603_1608Metric_MLZ1608M100WTD25; Mfg Part # MLP1608H2R2BT0S1
R6: 33k; R_0603_1608Metric_Square; Mfg Part # 0603WAF3302T5E
R7, R8, R9: 1M; R_0201_0603Metric_Square; Mfg Part # RC0201FR-071ML
TH1: Thermistor_NTC; R_0402_1005Metric_Square; Mfg Part # NCU15XH103F6SRC
U5: NPM1100-CAAA-R7; PARTREV V1.0
U6: XCL210C12; Mfg Part # XCL210C121GR-G

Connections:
+1V8: C33.1, L6.2, U5.B5 (VOUTB); also elsewhere on the board
+BATT: H5.1, U5.D1 (VBAT), U5.D2 (VBAT); also elsewhere on the board
/Audio/VDD_1V2: C34.1, U6.3 (VOUT), U6.8 (L2); also elsewhere on the board
/MCU/BATT_VOLTAGE: R8.2, R9.1; also elsewhere on the board
/MCU/PMIC_CHG: U5.E4 (CHG); also elsewhere on the board
/MCU/PMIC_ERR: U5.E3 (ERR); also elsewhere on the board
/MCU/PMIC_ISET: U5.D5 (ISET); also elsewhere on the board
/Power/BAT_NTC: TH1.1, U5.E1 (NTC)
/Power/CHG_CURRENT: R6.1, U5.E2 (ICHG)
/Power/VBUS: C30.1, H3.1, U5.B1 (VBUS), U5.B2 (VBUS)
/Power/VSYS: C32.1, C35.1, R7.1, U5.C1 (VSYS), U5.C2 (VSYS), U5.C3 (VTERMSET), U6.4 (CE), U6.6 (VIN)
GND: C30.2, C31.2, C32.2, C33.2, C34.2, C35.2, H4.1, H6.1, R6.2, R9.2, TH1.2, U5.A5 (PVSS), U5.B3 (VOUTBSET1), U5.B4 (VOUTBSET0), U5.C4 (AVSS), U5.C5 (AVSS), U5.D3 (SHPHLD), U5.D4 (SHPACT), U5.E5 (MODE), U6.2 (VSS), U6.5 (VSS), U6.9 (GND); also elsewhere on the board
unnamed: R7.2, R8.1
unnamed: C31.1, U5.A3 (DEC)
unnamed: L6.1, U5.A4 (SW)
unnamed: U6.1 (LX), U6.7 (L1)

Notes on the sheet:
VSYS is the input USB 5V (if plugged in) or battery voltage 3.7V (or lower)
Range 0-5V VSYS => 0-1.667V BATT_VOLTAGE Adjusted using 1/3 voltage divider No need for a capacitor as the microcontroller uses one internally. Current drain 1.123uA at 3.7V NOTE: We could use a 2 Meg 0402 basic component here
TODO: Explain GND1 (PVSS) Configuration 3 in nPM1100 spec
Battery Voltage Measurement
Battery Charger and 1.8V Converter
ISET = LOW (<= 100mA charge), HIGH (<= 500mA) USB power negotiation ERR = HIGH (temperature is out of range) CHG = HIGH (battery is charging)
1.2V DC/DC Converter
1.8V as per VOUTBSET pins
5V USB
Power Supply
40mAh 3.7V Li-ion Battery
Consider protecting with an ESD diode
VTERMSET = HIGH (charge at 4.2V) ICHG 10k (56 mA charge rate) ICHG 33k (18 mA charge rate) R = 625 / I - 1562.5 Set for small capacity battery (0.5C) Note: Consider using larger footprint for resistor for replaceability
Power Connectors
10k thermister should make thermal contact with battery to disable charging when temperature is out of range

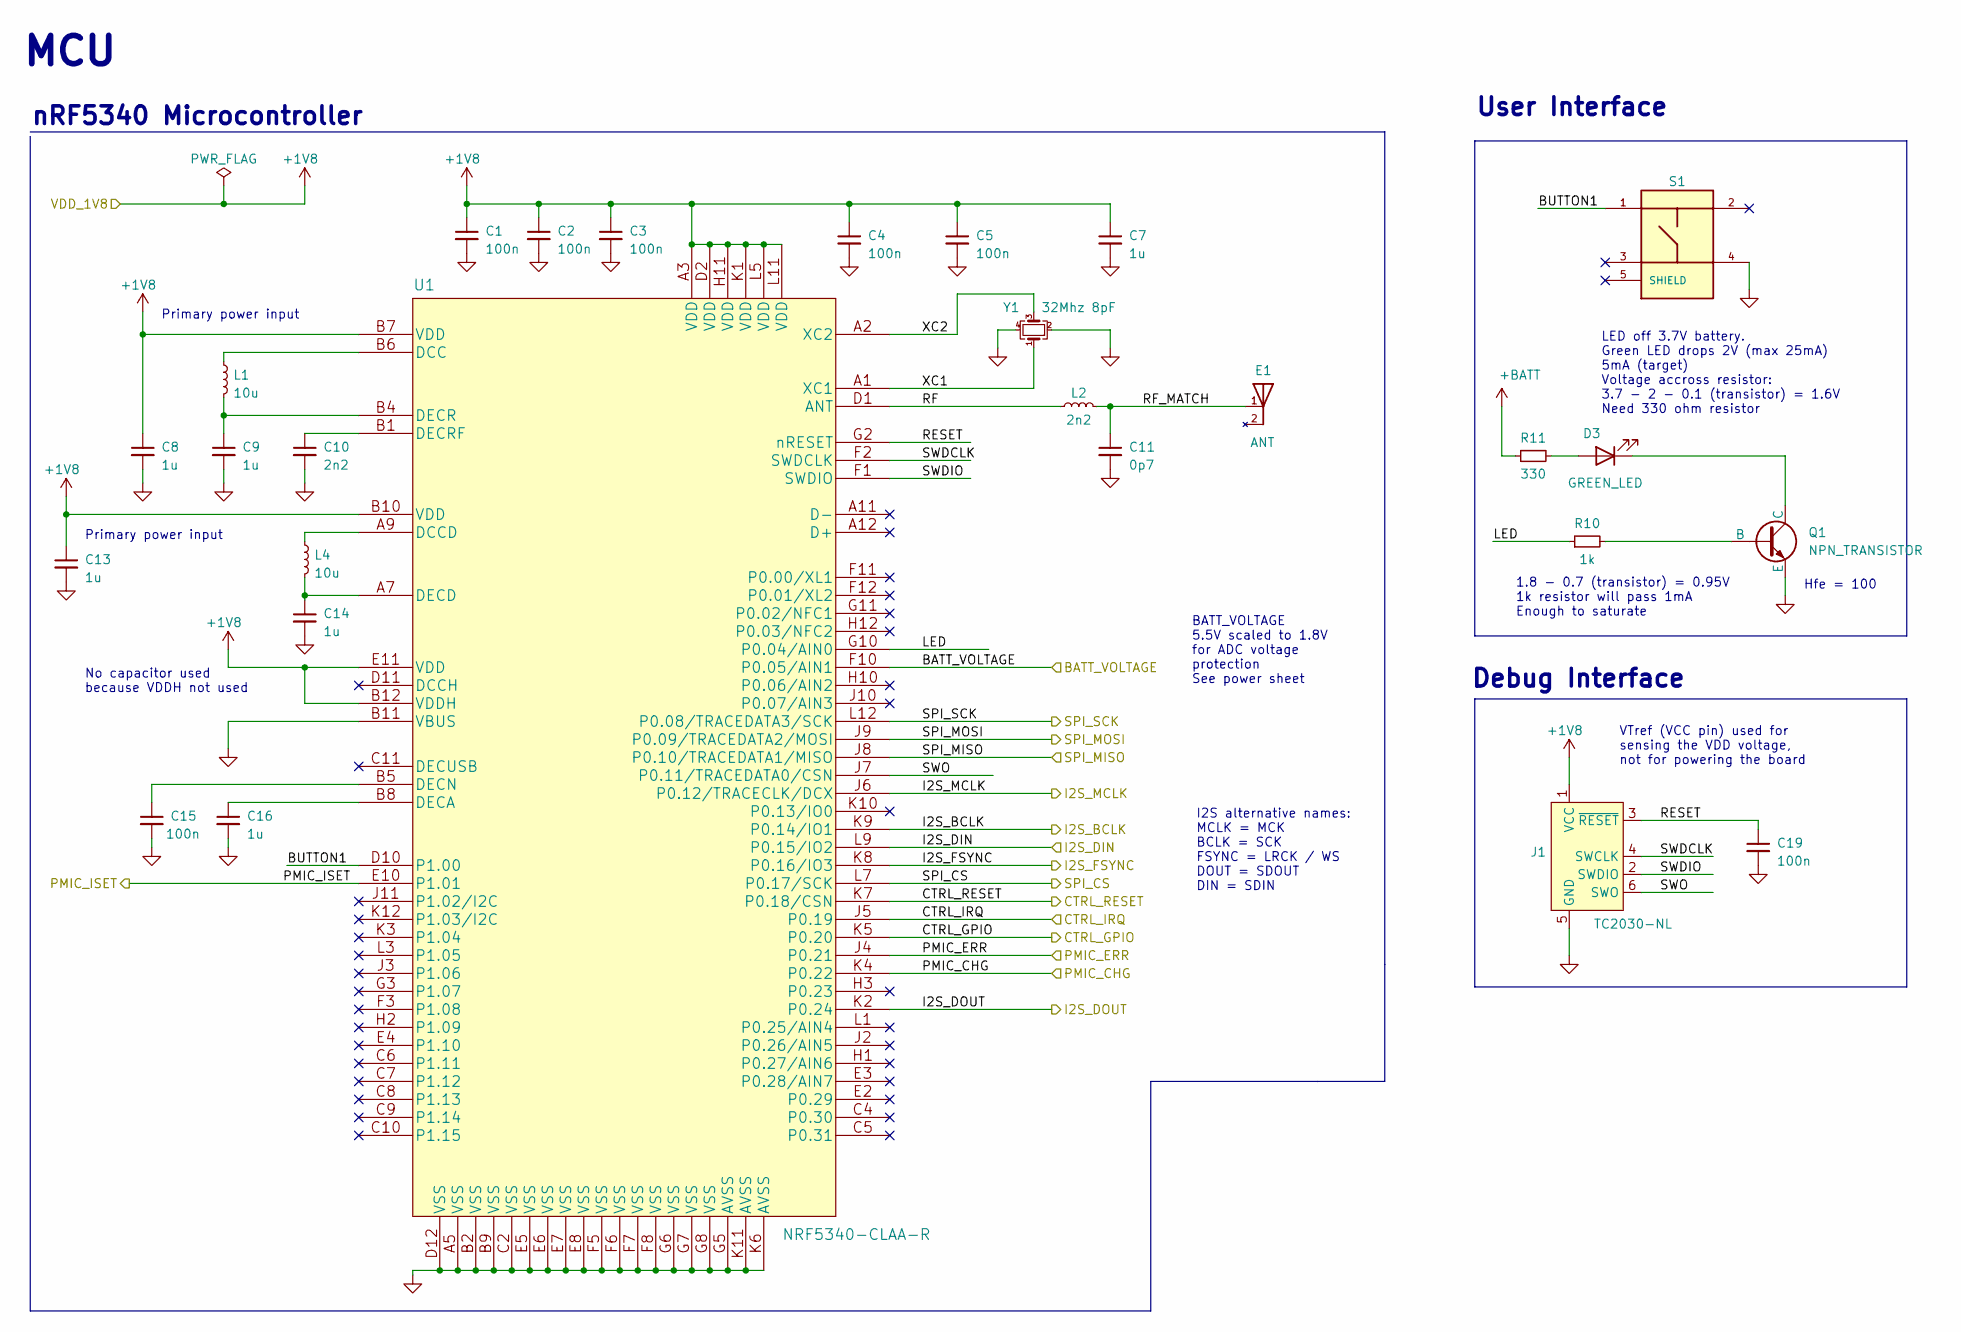
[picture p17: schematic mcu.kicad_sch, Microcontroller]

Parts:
C1, C2, C3, C4, C5, C15, C19: 100n; C_0201_0603Metric_Square; Mfg Part # GRM033R61A104KE15D
C7, C8, C9, C13, C14, C16: 1u; C_0402_1005Metric_Square; Mfg Part # GRM155R60J105KE19D
C10: 2n2; C_0201_0603Metric_Square; Mfg Part # GRM033R71A222KA01D
C11: 0p7; C_0201_0603Metric_Square; Mfg Part # GRM0335C1HR70WA01D
D3: GREEN_LED; LED_0402_1005Metric; Mfg Part # 16-213SYGC/S530-E3/TR8
E1: ANT; 2450AT18B100E; PARTREV 4.0
J1: TC2030-NL; Tag-Connect_TC2030-IDC-NL_2x03_P1.27mm_Vertical
L1, L4: 10u; L_0603_1608Metric_MLZ1608M100WTD25; Mfg Part # MLZ1608M100WTD25
L2: 2n2; L_0201_0603Metric_Square; Mfg Part # LQP03HQ2N2B02
Q1: NPN_TRANSISTOR; Npn_Transistor_TP5001P3; Mfg Part # TP5001P3
R10: 1k; R_0201_0603Metric_Square; Mfg Part # RC0201FR-071KL
R11: 330; R_0201_0603Metric_Square; Mfg Part # RC0201FR-07330RL
S1: PUSH_BTN; SW_PTS840GMSMTRLFS; Mfg Part # PTS840GMSMTRLFS
U1: NRF5340-CLAA-R; Mfg Part # NRF5340-CLAA
Y1: 32Mhz 8pF; MP06003_Crystal; Mfg Part # CX2016DB32000D0WZRC1

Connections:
+1V8: C1.1, C2.1, C3.1, C4.1, C5.1, C7.1, C8.1, C13.1, J1.1 (VCC), U1.A3 (VDD), U1.B7 (VDD), U1.B10 (VDD), U1.B12 (VDDH), U1.D2 (VDD), U1.E11 (VDD), U1.H11 (VDD), U1.K1 (VDD), U1.L5 (VDD), U1.L11 (VDD); also elsewhere on the board
+BATT: R11.1; also elsewhere on the board
/Audio/CTRL_GPIO: U1.K5 (P0.20); also elsewhere on the board
/Audio/CTRL_IRQ: U1.J5 (P0.19); also elsewhere on the board
/Audio/CTRL_RESET: U1.K7 (P0.18/CSN); also elsewhere on the board
/Audio/I2S_BCLK: U1.K9 (P0.14/IO1); also elsewhere on the board
/Audio/I2S_DIN: U1.K2 (P0.24); also elsewhere on the board
/Audio/I2S_DOUT: U1.L9 (P0.15/IO2); also elsewhere on the board
/Audio/I2S_FSYNC: U1.K8 (P0.16/IO3); also elsewhere on the board
/Audio/I2S_MCLK: U1.J6 (P0.12/TRACECLK/DCX); also elsewhere on the board
/Audio/SPI_CS: U1.L7 (P0.17/SCK); also elsewhere on the board
/Audio/SPI_MISO: U1.J8 (P0.10/TRACEDATA1/MISO); also elsewhere on the board
/Audio/SPI_MOSI: U1.J9 (P0.09/TRACEDATA2/MOSI); also elsewhere on the board
/Audio/SPI_SCK: U1.L12 (P0.08/TRACEDATA3/SCK); also elsewhere on the board
/MCU/BATT_VOLTAGE: U1.F10 (P0.05/AIN1); also elsewhere on the board
/MCU/BUTTON1: S1.1, U1.D10 (P1.00)
/MCU/LED: R10.1, U1.G10 (P0.04/AIN0)
/MCU/PMIC_CHG: U1.K4 (P0.22); also elsewhere on the board
/MCU/PMIC_ERR: U1.J4 (P0.21); also elsewhere on the board
/MCU/PMIC_ISET: U1.E10 (P1.01); also elsewhere on the board
/MCU/RESET: C19.1, J1.3 (~RESET), U1.G2 (nRESET)
/MCU/RF: L2.1, U1.D1 (ANT)
/MCU/RF_MATCH: C11.1, E1.1, L2.2
/MCU/SWDCLK: J1.4 (SWCLK), U1.F2 (SWDCLK)
/MCU/SWDIO: J1.2 (SWDIO), U1.F1 (SWDIO)
/MCU/SWO: J1.6 (SWO), U1.J7 (P0.11/TRACEDATA0/CSN)
/MCU/XC1: U1.A1 (XC1), Y1.1
/MCU/XC2: U1.A2 (XC2), Y1.3
GND: C1.2, C2.2, C3.2, C4.2, C5.2, C7.2, C8.2, C9.2, C10.2, C11.2, C13.2, C14.2, C15.2, C16.2, C19.2, J1.5 (GND), Q1.3 (E), S1.4, U1.A5 (VSS), U1.B2 (VSS), U1.B9 (VSS), U1.B11 (VBUS), U1.C2 (VSS), U1.D12 (VSS), U1.E5 (VSS), U1.E6 (VSS), U1.E7 (VSS), U1.E8 (VSS), U1.F5 (VSS), U1.F6 (VSS), U1.F7 (VSS), U1.F8 (VSS), U1.G5 (AVSS), U1.G6 (VSS), U1.G7 (VSS), U1.G8 (VSS), U1.K6 (AVSS), U1.K11 (AVSS), Y1.2, Y1.4; also elsewhere on the board
unnamed: D3.2 (A), R11.2
unnamed: D3.1 (K), Q1.1 (C)
unnamed: Q1.2 (B), R10.2
unnamed: L1.1, U1.B6 (DCC)
unnamed: L4.1, U1.A9 (DCCD)
unnamed: C16.1, U1.B8 (DECA)
unnamed: C14.1, L4.2, U1.A7 (DECD)
unnamed: C15.1, U1.B5 (DECN)
unnamed: C9.1, L1.2, U1.B4 (DECR)
unnamed: C10.1, U1.B1 (DECRF)

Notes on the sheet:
LED off 3.7V battery. Green LED drops 2V (max 25mA) 5mA (target) Voltage accross resistor: 3.7 - 2 - 0.1 (transistor) = 1.6V Need 330 ohm resistor
BATT_VOLTAGE 5.5V scaled to 1.8V for ADC voltage protection See power sheet
VTref (VCC pin) used for sensing the VDD voltage, not for powering the board
1.8 - 0.7 (transistor) = 0.95V 1k resistor will pass 1mA Enough to saturate
I2S alternative names: MCLK = MCK BCLK = SCK FSYNC = LRCK / WS DOUT = SDOUT DIN = SDIN
No capacitor used because VDDH not used
MCU
Debug Interface
Primary power input
Hfe = 100
User Interface
nRF5340 Microcontroller

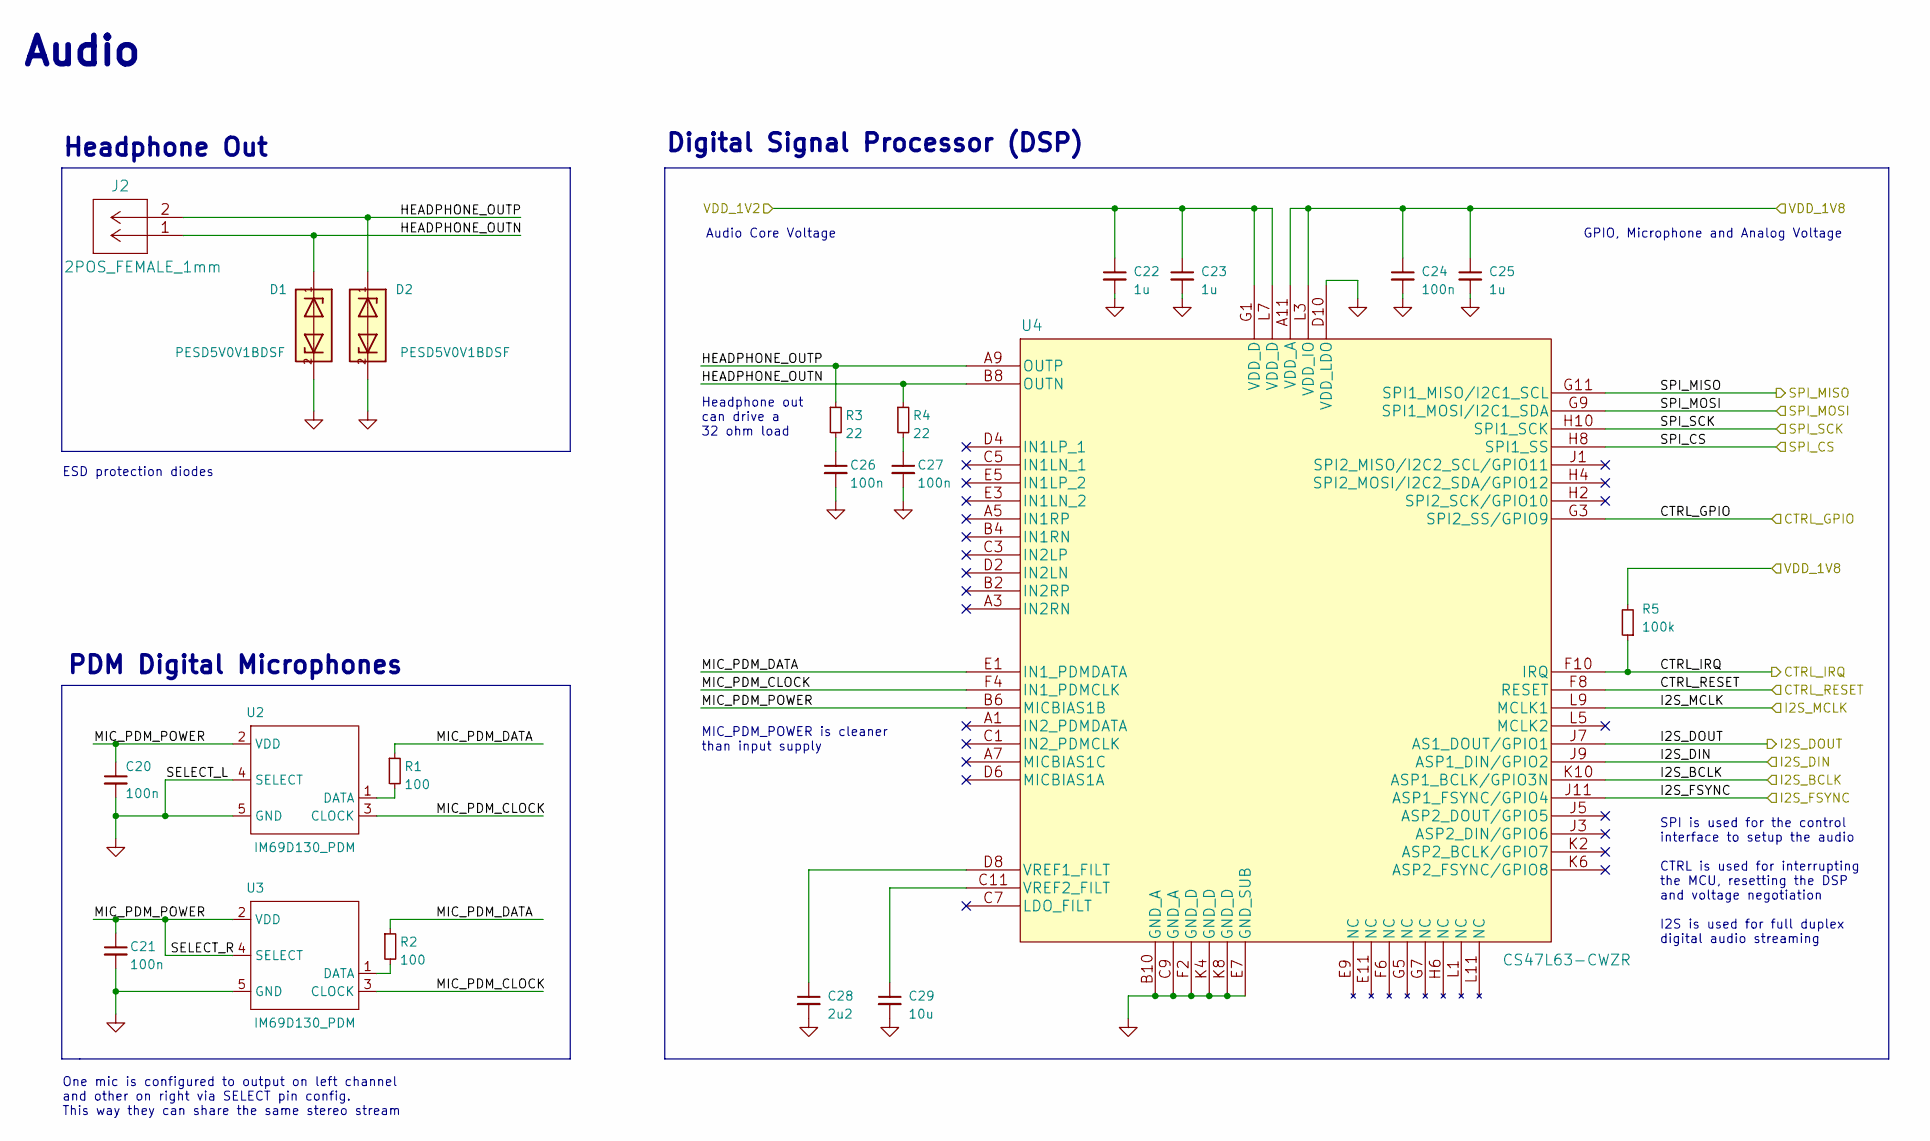
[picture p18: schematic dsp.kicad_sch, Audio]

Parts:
C20, C21, C24, C26, C27: 100n; C_0201_0603Metric_Square; Mfg Part # GRM033R61A104KE15D
C22, C23, C25: 1u; C_0402_1005Metric_Square; Mfg Part # GRM155R60J105KE19D
C28: 2u2; C_0402_1005Metric_Square; Mfg Part # GRM155R61A225KE95D
C29: 10u; C_0603_1608Metric_Square; Mfg Part # GRM188R61A106KE69D
D1, D2: PESD5V0V1BDSF; D_0603_1608Metric_Square; Mfg Part # PESD5V0V1BDSF,315
J2: 2POS_FEMALE_1mm; BC075-02-A-L-A; Mfg Part # BC075-02-A-L-A
R1, R2: 100; R_0201_0603Metric_Square; Mfg Part # RC0201FR-07100RL
R3, R4: 22; R_0201_0603Metric_Square; Mfg Part # RC0201FR-0722RL
R5: 100k; R_0201_0603Metric_Square; Mfg Part # RC0201FR-07100KL
U2, U3: IM69D130_PDM; MIC_IM69D130V01XTSA1_PadFix_Round; Mfg Part # IM69D130V01XTSA1
U4: CS47L63-CWZR; Mfg Part # CS47L63-CWZR

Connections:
+1V8: C24.1, C25.1, R5.2, U4.A11 (VDD_A), U4.L3 (VDD_IO); also elsewhere on the board
/Audio/CTRL_GPIO: U4.G3 (SPI2_SS/GPIO9); also elsewhere on the board
/Audio/CTRL_IRQ: R5.1, U4.F10 (IRQ); also elsewhere on the board
/Audio/CTRL_RESET: U4.F8 (RESET); also elsewhere on the board
/Audio/HEADPHONE_OUTN: D1.1, J2.1, R4.1, U4.B8 (OUTN)
/Audio/HEADPHONE_OUTP: D2.1, J2.2, R3.1, U4.A9 (OUTP)
/Audio/I2S_BCLK: U4.K10 (ASP1_BCLK/GPIO3N); also elsewhere on the board
/Audio/I2S_DIN: U4.J9 (ASP1_DIN/GPIO2); also elsewhere on the board
/Audio/I2S_DOUT: U4.J7 (AS1_DOUT/GPIO1); also elsewhere on the board
/Audio/I2S_FSYNC: U4.J11 (ASP1_FSYNC/GPIO4); also elsewhere on the board
/Audio/I2S_MCLK: U4.L9 (MCLK1); also elsewhere on the board
/Audio/MIC_PDM_CLOCK: U2.3 (CLOCK), U3.3 (CLOCK), U4.F4 (IN1_PDMCLK)
/Audio/MIC_PDM_DATA: R1.1, R2.1, U4.E1 (IN1_PDMDATA)
/Audio/MIC_PDM_POWER: C20.1, C21.1, U2.2 (VDD), U3.2 (VDD), U3.4 (SELECT), U4.B6 (MICBIAS1B)
/Audio/SPI_CS: U4.H8 (SPI1_SS); also elsewhere on the board
/Audio/SPI_MISO: U4.G11 (SPI1_MISO/I2C1_SCL); also elsewhere on the board
/Audio/SPI_MOSI: U4.G9 (SPI1_MOSI/I2C1_SDA); also elsewhere on the board
/Audio/SPI_SCK: U4.H10 (SPI1_SCK); also elsewhere on the board
/Audio/VDD_1V2: C22.1, C23.1, U4.G1 (VDD_D), U4.L7 (VDD_D); also elsewhere on the board
GND: C20.2, C21.2, C22.2, C23.2, C24.2, C25.2, C26.2, C27.2, C28.2, C29.2, D1.2, D2.2, U2.4 (SELECT), U2.5 (GND), U3.5 (GND), U4.B10 (GND_A), U4.C9 (GND_A), U4.D10 (VDD_LDO), U4.E7 (GND_SUB), U4.F2 (GND_D), U4.K4 (GND_D), U4.K8 (GND_D); also elsewhere on the board
unnamed: C26.1, R3.2
unnamed: C27.1, R4.2
unnamed: R1.2, U2.1 (DATA)
unnamed: R2.2, U3.1 (DATA)
unnamed: C28.1, U4.D8 (VREF1_FILT)
unnamed: C29.1, U4.C11 (VREF2_FILT)

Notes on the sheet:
Digital Signal Processor (DSP)
One mic is configured to output on left channel and other on right via SELECT pin config. This way they can share the same stereo stream
SPI is used for the control interface to setup the audio CTRL is used for interrupting the MCU, resetting the DSP and voltage negotiation I2S is used for full duplex digital audio streaming
GPIO, Microphone and Analog Voltage
Audio Core Voltage
Audio
Headphone out can drive a 32 ohm load
Headphone Out
ESD protection diodes
MIC_PDM_POWER is cleaner than input supply
PDM Digital Microphones

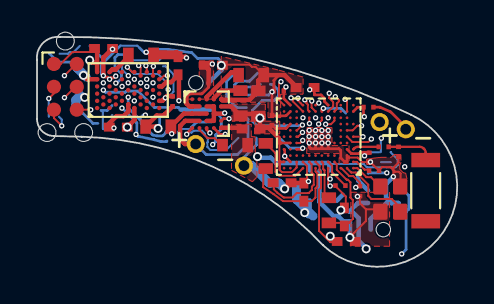
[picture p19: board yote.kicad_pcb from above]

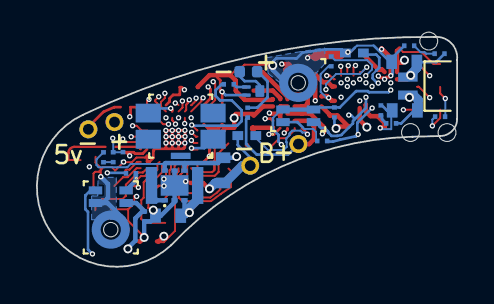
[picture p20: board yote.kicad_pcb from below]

Board: 8 copper layers, 23.4 x 12.8 mm, 66 parts (28 on the bottom side), 59 nets.

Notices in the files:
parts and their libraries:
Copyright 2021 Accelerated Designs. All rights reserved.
